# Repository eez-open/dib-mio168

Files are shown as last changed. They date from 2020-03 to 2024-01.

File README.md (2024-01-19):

### Ownership and License
The contributors are listed in CONTRIB.TXT.

Licenses | OSHWA UID
--|--
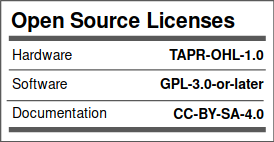
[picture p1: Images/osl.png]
osl
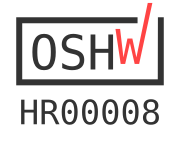
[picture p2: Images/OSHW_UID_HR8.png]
OSHW-HR000008 (https://certification.oshwa.org/hr000008.html)
 | 

### Overview

The [EEZ DIB](https://github.com/eez-open/modular-psu) MIO168 module features multiple digital I/O, analog outputs and expansion connectors for carry various AFEs.

### Feature list

* On-board [STM32F446ZCT6](https://www.st.com/content/st_com/en/products/microcontrollers-microprocessors/stm32-32-bit-arm-cortex-mcus/stm32-high-performance-mcus/stm32f4-series/stm32f446/stm32f446zc.html) high-performance foundation line MCU, ARM Cortex-M4 with DSP and FPU, 256 KiB Flash, LQFP-144 package 
* 1 x 8-pin single row 3.81 mm connector (digital inputs)
* 1 x 16-pin dual row 3.81 mm I/O connector (digital and analog outputs)
* 2 x 10-pin ADIB 2.0 mm connectors
* 8 x protected digital inputs (3.3/5/24 V), 2 x fast/slow, 6 x slow
* 8 x digital outputs (low-side) with multiple protections, voltage clamp 42V, current limit 10 A
* 2 x PWM outputs (protected) or sensor bias power (+/-15 V, max. 10 mA)
* 2 x analog bipolar outputs (+/-5 V, +/-10 V, 0-5 V, 0-10 V). Voltage or current output with protection. 12-bit DAC, replaceable with pin compatible 14- or 16-bit version
* 2 x analog bipolar outputs +/-10 V. 12-bit DAC, replaceable with pin compatible 14- or 16-bit version
* On-board isolated power supply with +/-5.3 V outputs (with 4x multipliers), +/-15 V and +3.3 V LDO
* Firmware download via SPI
* Optional SWD for debugging
* I2C EEPROM for storing board specific parameters
* Dimensions: 146 x 95 mm, 4-layer PCB

### r3B1 prototype 3D model (without AFE installed)

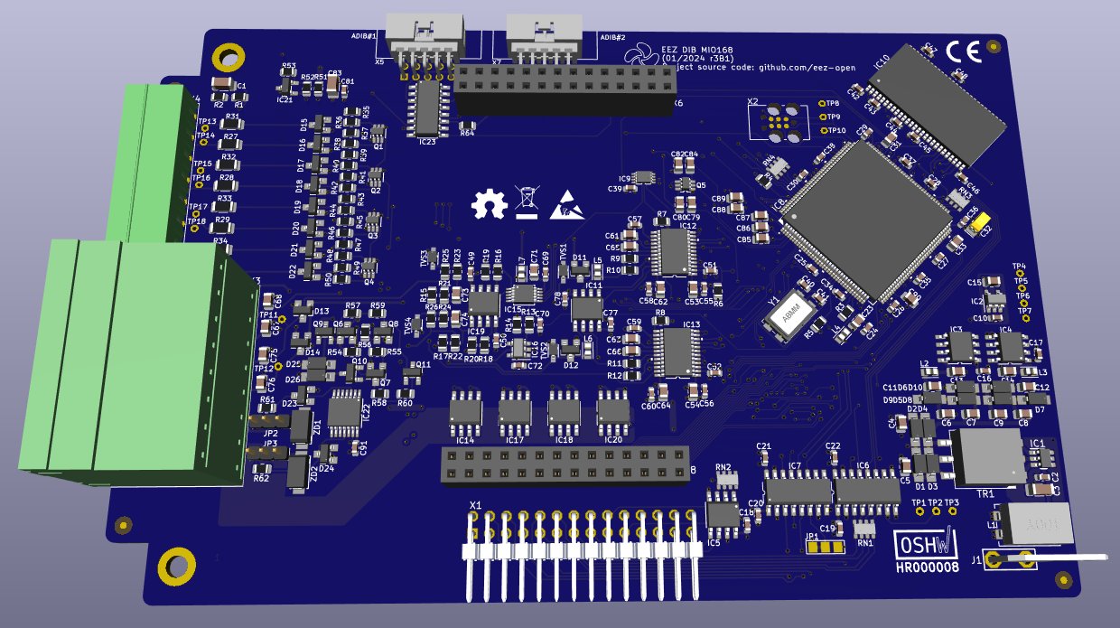
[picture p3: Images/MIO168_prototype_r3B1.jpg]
prototype


### Firmware repository

https://github.com/eez-open/dib-mio168-fw  
The firmware download procedure is described in [Chapter 13.2](https://www.envox.eu/eez-bench-box-3/bb3-user-manual/13-firmware-upgrade/#bb3_man_module_upgrade) of the User Manual.  
The MIO168 module GUI is described in [Chapter 19](https://www.envox.eu/eez-bench-box-3/bb3-user-manual/19-mio168-mixed-input-output-module/) of the User Manual. 

### KiCad project (v7 or newer)

* [MIO168 r3B1](https://github.com/eez-open/dib-mio168/tree/master/EDA%20files/KiCad)

All symbols, footprints and 3D models used in the project can be found in the [EEZ-DIB Library](https://github.com/eez-open/eez-kicad-libraries) plugin for KiCad.

### Bill of materials

* [Download](https://github.com/eez-open/dib-mio168/tree/master/EDA%20files/KiCad/bom/ibom.html) as raw file _Interactive BOM_ (ibom.html) and open it locally in your browser.

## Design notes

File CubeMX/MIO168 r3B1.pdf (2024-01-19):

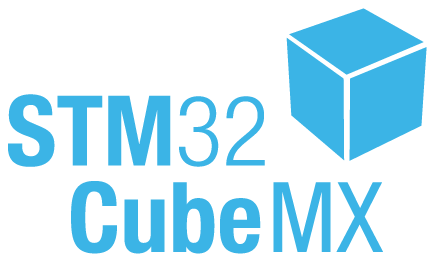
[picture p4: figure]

19/01/2024

MIO168 r3B1 Project
Configuration Report

## 1. Description

### 1.1. Project

Project Name | MIO168 r3B1
Board Name | custom
Generated with: | STM32CubeMX 6.10.0
Date | 01/19/2024

### 1.2. MCU

MCU Series | STM32F4
MCU Line | STM32F446
MCU name | STM32F446ZCTx
MCU Package | LQFP144
MCU Pin number | 144

### 1.3. Core(s) information

Core(s) | Arm Cortex-M4

## 2. Pinout Configuration

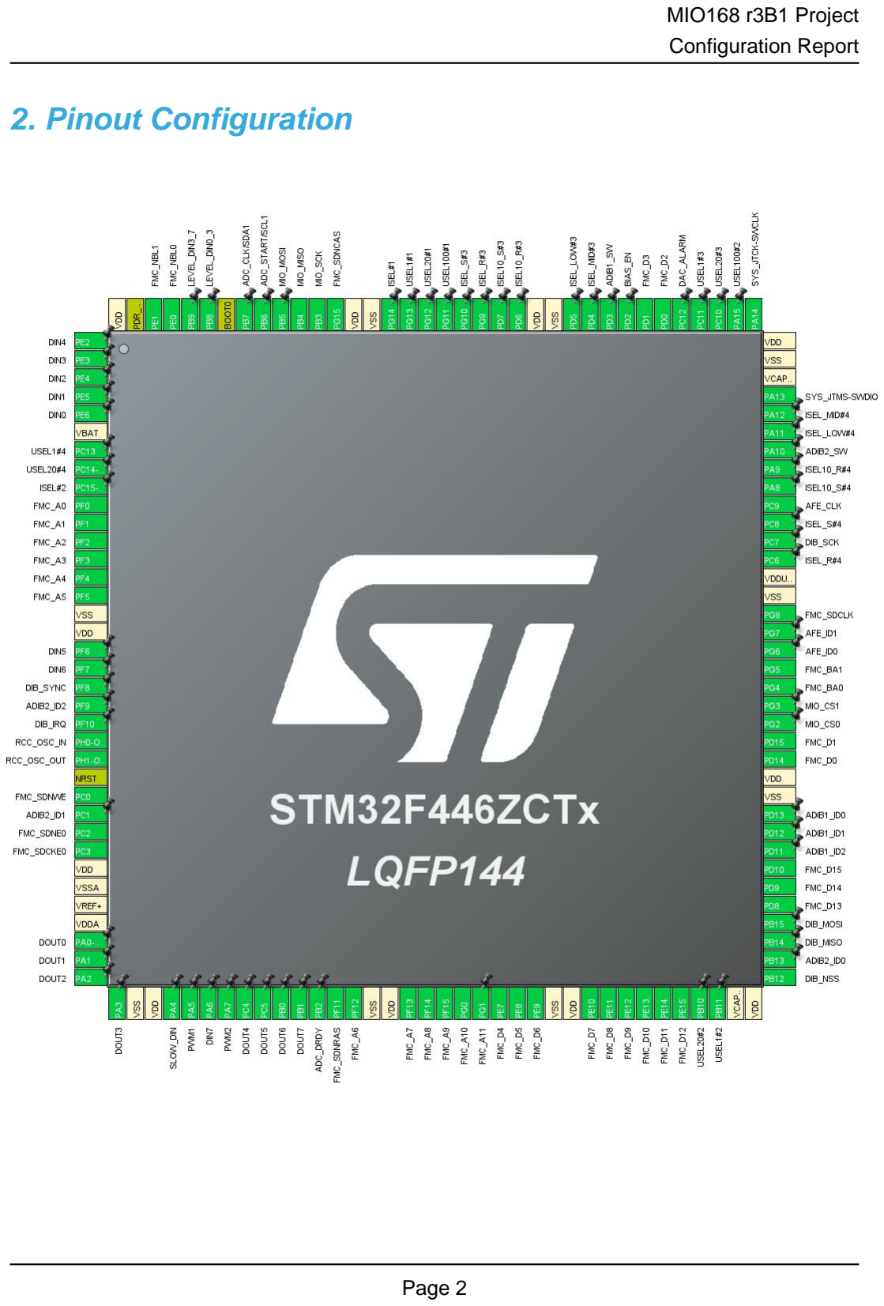
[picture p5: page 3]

## 3. Pins Configuration

Pin Number LQFP144 | Pin Name (function after reset) | Pin Type | Alternate Function(s) | Label
1 | PE2 * | I/O | GPIO_Input | DIN4
2 | PE3 * | I/O | GPIO_Input | DIN3
3 | PE4 * | I/O | GPIO_Input | DIN2
4 | PE5 | I/O | TIM9_CH1 | DIN1
5 | PE6 | I/O | TIM9_CH2 | DIN0
6 | VBAT | Power
7 | PC13 * | I/O | GPIO_Output | USEL1#4
8 | PC14-OSC32_IN * | I/O | GPIO_Output | USEL20#4
9 | PC15-OSC32_OUT * | I/O | GPIO_Output | ISEL#2
10 | PF0 | I/O | FMC_A0
11 | PF1 | I/O | FMC_A1
12 | PF2 | I/O | FMC_A2
13 | PF3 | I/O | FMC_A3
14 | PF4 | I/O | FMC_A4
15 | PF5 | I/O | FMC_A5
16 | VSS | Power
17 | VDD | Power
18 | PF6 * | I/O | GPIO_Input | DIN5
19 | PF7 * | I/O | GPIO_Input | DIN6
20 | PF8 * | I/O | GPIO_Input | DIB_SYNC
21 | PF9 * | I/O | GPIO_Input | ADIB2_ID2
22 | PF10 * | I/O | GPIO_Output | DIB_IRQ
23 | PH0-OSC_IN | I/O | RCC_OSC_IN
24 | PH1-OSC_OUT | I/O | RCC_OSC_OUT
25 | NRST | Reset
26 | PC0 | I/O | FMC_SDNWE
27 | PC1 * | I/O | GPIO_Input | ADIB2_ID1
28 | PC2 | I/O | FMC_SDNE0
29 | PC3 | I/O | FMC_SDCKE0
30 | VDD | Power
31 | VSSA | Power
32 | VREF+ | Power
33 | VDDA | Power
34 | PA0-WKUP * | I/O | GPIO_Output | DOUT0
35 | PA1 * | I/O | GPIO_Output | DOUT1
36 | PA2 * | I/O | GPIO_Output | DOUT2

Pin Number LQFP144 | Pin Name (function after reset) | Pin Type | Alternate Function(s) | Label
37 | PA3 * | I/O | GPIO_Output | DOUT3
38 | VSS | Power
39 | VDD | Power
40 | PA4 * | I/O | GPIO_Output | SLOW_DIN
41 | PA5 | I/O | TIM2_CH1 | PWM1
42 | PA6 * | I/O | GPIO_Input | DIN7
43 | PA7 | I/O | TIM3_CH2 | PWM2
44 | PC4 * | I/O | GPIO_Output | DOUT4
45 | PC5 * | I/O | GPIO_Output | DOUT5
46 | PB0 * | I/O | GPIO_Output | DOUT6
47 | PB1 * | I/O | GPIO_Output | DOUT7
48 | PB2 * | I/O | GPIO_Input | ADC_DRDY
49 | PF11 | I/O | FMC_SDNRAS
50 | PF12 | I/O | FMC_A6
51 | VSS | Power
52 | VDD | Power
53 | PF13 | I/O | FMC_A7
54 | PF14 | I/O | FMC_A8
55 | PF15 | I/O | FMC_A9
56 | PG0 | I/O | FMC_A10
57 | PG1 | I/O | FMC_A11
58 | PE7 | I/O | FMC_D4
59 | PE8 | I/O | FMC_D5
60 | PE9 | I/O | FMC_D6
61 | VSS | Power
62 | VDD | Power
63 | PE10 | I/O | FMC_D7
64 | PE11 | I/O | FMC_D8
65 | PE12 | I/O | FMC_D9
66 | PE13 | I/O | FMC_D10
67 | PE14 | I/O | FMC_D11
68 | PE15 | I/O | FMC_D12
69 | PB10 * | I/O | GPIO_Output | USEL20#2
70 | PB11 * | I/O | GPIO_Output | USEL1#2
71 | VCAP_1 | Power
72 | VDD | Power
73 | PB12 | I/O | SPI2_NSS | DIB_NSS
74 | PB13 * | I/O | GPIO_Input | ADIB2_ID0
75 | PB14 | I/O | SPI2_MISO | DIB_MISO

Pin Number LQFP144 | Pin Name (function after reset) | Pin Type | Alternate Function(s) | Label
76 | PB15 | I/O | SPI2_MOSI | DIB_MOSI
77 | PD8 | I/O | FMC_D13
78 | PD9 | I/O | FMC_D14
79 | PD10 | I/O | FMC_D15
80 | PD11 * | I/O | GPIO_Input | ADIB1_ID2
81 | PD12 * | I/O | GPIO_Input | ADIB1_ID1
82 | PD13 * | I/O | GPIO_Input | ADIB1_ID0
83 | VSS | Power
84 | VDD | Power
85 | PD14 | I/O | FMC_D0
86 | PD15 | I/O | FMC_D1
87 | PG2 * | I/O | GPIO_Output | MIO_CS0
88 | PG3 * | I/O | GPIO_Output | MIO_CS1
89 | PG4 | I/O | FMC_BA0
90 | PG5 | I/O | FMC_BA1
91 | PG6 * | I/O | GPIO_Input | AFE_ID0
92 | PG7 * | I/O | GPIO_Input | AFE_ID1
93 | PG8 | I/O | FMC_SDCLK
94 | VSS | Power
95 | VDDUSB | Power
96 | PC6 * | I/O | GPIO_Output | ISEL_R#4
97 | PC7 | I/O | SPI2_SCK | DIB_SCK
98 | PC8 * | I/O | GPIO_Output | ISEL_S#4
99 | PC9 | I/O | RCC_MCO_2 | AFE_CLK
100 | PA8 * | I/O | GPIO_Output | ISEL10_S#4
101 | PA9 * | I/O | GPIO_Output | ISEL10_R#4
102 | PA10 * | I/O | GPIO_Output | ADIB2_SW
103 | PA11 * | I/O | GPIO_Output | ISEL_LOW#4
104 | PA12 * | I/O | GPIO_Output | ISEL_MID#4
105 | PA13 | I/O | SYS_JTMS-SWDIO
106 | VCAP_2 | Power
107 | VSS | Power
108 | VDD | Power
109 | PA14 | I/O | SYS_JTCK-SWCLK
110 | PA15 * | I/O | GPIO_Output | USEL100#2
111 | PC10 * | I/O | GPIO_Output | USEL20#3
112 | PC11 * | I/O | GPIO_Output | USEL1#3
113 | PC12 * | I/O | GPIO_Input | DAC_ALARM
114 | PD0 | I/O | FMC_D2

Pin Number LQFP144 | Pin Name (function after reset) | Pin Type | Alternate Function(s) | Label
115 | PD1 | I/O | FMC_D3
116 | PD2 * | I/O | GPIO_Output | BIAS_EN
117 | PD3 * | I/O | GPIO_Output | ADIB1_SW
118 | PD4 * | I/O | GPIO_Output | ISEL_MID#3
119 | PD5 * | I/O | GPIO_Output | ISEL_LOW#3
120 | VSS | Power
121 | VDD | Power
122 | PD6 * | I/O | GPIO_Output | ISEL10_R#3
123 | PD7 * | I/O | GPIO_Output | ISEL10_S#3
124 | PG9 * | I/O | GPIO_Output | ISEL_R#3
125 | PG10 * | I/O | GPIO_Output | ISEL_S#3
126 | PG11 * | I/O | GPIO_Output | USEL100#1
127 | PG12 * | I/O | GPIO_Output | USEL20#1
128 | PG13 * | I/O | GPIO_Output | USEL1#1
129 | PG14 * | I/O | GPIO_Output | ISEL#1
130 | VSS | Power
131 | VDD | Power
132 | PG15 | I/O | FMC_SDNCAS
133 | PB3 | I/O | SPI3_SCK | MIO_SCK
134 | PB4 | I/O | SPI3_MISO | MIO_MISO
135 | PB5 | I/O | SPI3_MOSI | MIO_MOSI
136 | PB6 * | I/O | GPIO_Output | ADC_START/SCL1
137 | PB7 * | I/O | GPIO_Output | ADC_CLK/SDA1
138 | BOOT0 | Boot
139 | PB8 * | I/O | GPIO_Output | LEVEL_DIN0_3
140 | PB9 * | I/O | GPIO_Output | LEVEL_DIN3_7
141 | PE0 | I/O | FMC_NBL0
142 | PE1 | I/O | FMC_NBL1
143 | PDR_ON | Reset
144 | VDD | Power

* The pin is affected with an I/O function

## 4. Clock Tree Configuration

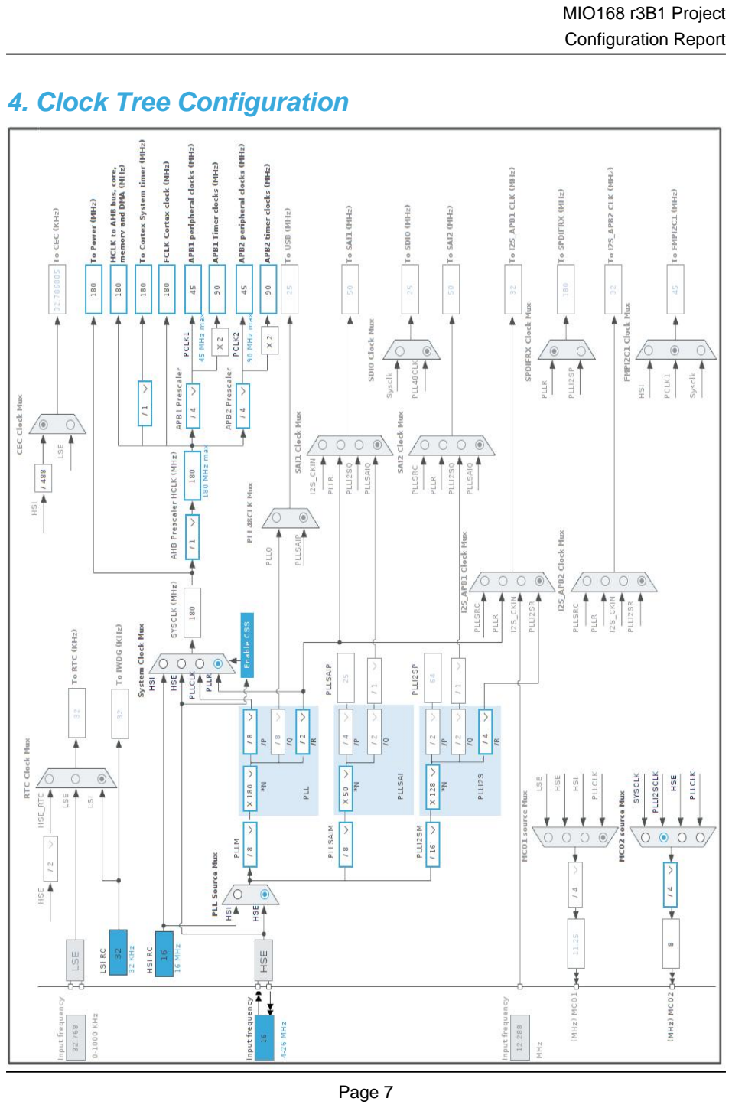
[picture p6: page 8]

## 5. Software Project

### 5.1. Project Settings

Name | Value
Project Name | MIO168 r3B1
Project Folder | /home/denis/git-public/dib-mio168/CubeMX
Toolchain / IDE | STM32CubeIDE
Firmware Package Name and Version | STM32Cube FW_F4 V1.26.1
Application Structure | Advanced
Generate Under Root | Yes
Do not generate the main() | No
Minimum Heap Size | 0x2000
Minimum Stack Size | 0x4000

### 5.2. Code Generation Settings

Name | Value
STM32Cube MCU packages and embedded software | Copy only the necessary library files
Generate peripheral initialization as a pair of '.c/.h' files | No
Backup previously generated files when re-generating | No
Keep User Code when re-generating | Yes
Delete previously generated files when not re-generated | Yes
Set all free pins as analog (to optimize the power consumption) | No
Enable Full Assert | No

### 5.3. Advanced Settings - Generated Function Calls

Rank | Function Name | Peripheral Instance Name
1 | MX_GPIO_Init | GPIO
2 | MX_DMA_Init | DMA
3 | SystemClock_Config | RCC
4 | MX_CRC_Init | CRC
5 | MX_SPI2_Init | SPI2
6 | MX_SPI3_Init | SPI3
7 | MX_TIM9_Init | TIM9
8 | MX_TIM6_Init | TIM6
9 | MX_TIM2_Init | TIM2
10 | MX_TIM3_Init | TIM3
11 | MX_TIM7_Init | TIM7

Rank | Function Name | Peripheral Instance Name
12 | MX_FMC_Init | FMC

## 1. Power Consumption Calculator report

### 1.1. Microcontroller Selection

Series | STM32F4
Line | STM32F446
MCU | STM32F446ZCTx
Datasheet | DS10693_Rev6

### 1.2. Parameter Selection

Temperature | 25
Vdd | 3.3

### 1.3. Battery Selection

Battery | Li-SOCL2(A3400)
Capacity | 3400.0 mAh
Self Discharge | 0.08 %/month
Nominal Voltage | 3.6 V
Max Cont Current | 100.0 mA
Max Pulse Current | 200.0 mA
Cells in series | 1
Cells in parallel | 1

### 1.4. Sequence

Step | Step1 | Step2
Mode | RUN | STOP_UDM (Under Drive)
Vdd | 3.3 | 3.3
Voltage Source | Battery | Battery
Range | Scale1-High | No Scale
Fetch Type | RAM/FLASH/REGON/ART/P REFETCH | n/a
CPU Frequency | 180 MHz | 0 Hz
Clock Configuration | HSE PLL | Regulator_LP Flash-PwrDwn
Clock Source Frequency | 4 MHz | 0 Hz
Peripherals
Additional Cons. | 0 mA | 0 mA
Average Current | 46 mA | 55 µA
Duration | 0.1 ms | 0.9 ms
DMIPS | 225.0 | 0.0
Ta Max | 99.99 | 104.99
Category | In DS Table | In DS Table

### 1.5. Results

Sequence Time | 1 ms | Average Current | 4.65 mA
Battery Life | 1 month | Average DMIPS | 225.0 DMIPS

### 1.6. Chart

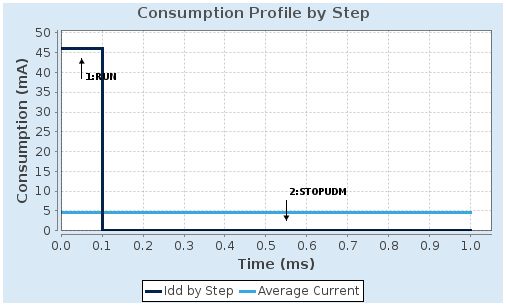
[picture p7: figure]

## 2. Peripherals and Middlewares Configuration

### 2.1. CRC

mode: Activated

### 2.2. FMC

SDRAM 1
Clock and chip enable: SDCKE0+SDNE0 Internal bank number: 4 banks Address: 12 bits
Data: 16 bits
Byte enable: set
2.2.1. SDRAM 1:

SDRAM control:

Bank | SDRAM bank 1
Number of column address bits | 8 bits
Number of row address bits | 12 bits
CAS latency | 1 memory clock cycle
Write protection | Disabled
SDRAM common clock | Disabled
SDRAM common burst read | Disabled
SDRAM common read pipe delay | 0 HCLK clock cycle
SDRAM timing in memory clock cycles:
Load mode register to active delay | 16
Exit self-refresh delay | 16
Self-refresh time | 16
SDRAM common row cycle delay | 16
Write recovery time | 16
SDRAM common row precharge delay | 16
Row to column delay | 16

### 2.3. RCC

High Speed Clock (HSE): Crystal/Ceramic Resonator mode: Master Clock Output 2
2.3.1. Parameter Settings:

System Parameters:

VDD voltage (V) | 3.3
Instruction Cache | Enabled
Prefetch Buffer | Enabled
Data Cache | Enabled
Flash Latency(WS) | 5 WS (6 CPU cycle)
RCC Parameters:
HSI Calibration Value | 16
TIM Prescaler Selection | Disabled
HSE Startup Timout Value (ms) | 100
LSE Startup Timout Value (ms) | 5000
Power Parameters:
Power Regulator Voltage Scale | Power Regulator Voltage Scale 1
Power Over Drive | Enabled

### 2.4. SPI2

Mode: Full-Duplex Slave
Hardware NSS Signal: Hardware NSS Input Signal
2.4.1. Parameter Settings:

Basic Parameters:

Frame Format | Motorola
Data Size | 8 Bits
First Bit | MSB First
Clock Parameters:
Clock Polarity (CPOL) | Low
Clock Phase (CPHA) | 1 Edge
Advanced Parameters:
CRC Calculation | Disabled
NSS Signal Type | Input Hardware

### 2.5. SPI3

Mode: Full-Duplex Master
2.5.1. Parameter Settings:

Basic Parameters:

Frame Format | Motorola
Data Size | 8 Bits

First Bit | MSB First
Clock Parameters:
Prescaler (for Baud Rate) | 2
Baud Rate | 22.5 MBits/s *
Clock Polarity (CPOL) | Low
Clock Phase (CPHA) | 2 Edge *
Advanced Parameters:
CRC Calculation | Disabled
NSS Signal Type | Software

### 2.6. SYS

Debug: Serial Wire
Timebase Source: SysTick

### 2.7. TIM2

Channel1: PWM Generation CH1
2.7.1. Parameter Settings:

Counter Settings:

Prescaler (PSC - 16 bits value) | 0
Counter Mode | Up
Counter Period (AutoReload Register - 32 bits value ) | 0 *
Internal Clock Division (CKD) | No Division
auto-reload preload | Disable
Trigger Output (TRGO) Parameters:
Master/Slave Mode (MSM bit) | Disable (Trigger input effect not delayed)
Trigger Event Selection | Reset (UG bit from TIMx_EGR)
PWM Generation Channel 1:
Mode | PWM mode 1
Pulse (32 bits value) | 0
Output compare preload | Enable
Fast Mode | Disable
CH Polarity | High

### 2.8. TIM3

Channel2: PWM Generation CH2
2.8.1. Parameter Settings:

Counter Settings:

Prescaler (PSC - 16 bits value) | 0
Counter Mode | Up
Counter Period (AutoReload Register - 16 bits value ) | 0 *
Internal Clock Division (CKD) | No Division
auto-reload preload | Disable
Trigger Output (TRGO) Parameters:
Master/Slave Mode (MSM bit) | Disable (Trigger input effect not delayed)
Trigger Event Selection | Reset (UG bit from TIMx_EGR)
PWM Generation Channel 2:
Mode | PWM mode 1
Pulse (16 bits value) | 0
Output compare preload | Enable
Fast Mode | Disable
CH Polarity | High

### 2.9. TIM6

mode: Activated
2.9.1. Parameter Settings:

Counter Settings:

Prescaler (PSC - 16 bits value) | 8 *
Counter Mode | Up
Counter Period (AutoReload Register - 16 bits value ) | 999 *
auto-reload preload | Enable *
Trigger Output (TRGO) Parameters:
Trigger Event Selection | Reset (UG bit from TIMx_EGR)

### 2.10. TIM7

mode: Activated
2.10.1. Parameter Settings:

Counter Settings:

Prescaler (PSC - 16 bits value) | 8 *
Counter Mode | Up
Counter Period (AutoReload Register - 16 bits value ) | 999 *
auto-reload preload | Enable *
Trigger Output (TRGO) Parameters:
Trigger Event Selection | Reset (UG bit from TIMx_EGR)

### 2.11. TIM9

Channel1: Input Capture direct mode
Channel2: Input Capture direct mode
2.11.1. Parameter Settings:

Counter Settings:

Prescaler (PSC - 16 bits value) | 0
Counter Mode | Up
Counter Period (AutoReload Register - 16 bits value ) | 0 *
Internal Clock Division (CKD) | No Division
auto-reload preload | Disable
Input Capture Channel 1:
Polarity Selection | Rising Edge
IC Selection | Direct
Prescaler Division Ratio | No division
Input Filter (4 bits value) | 0
Input Capture Channel 2:
Polarity Selection | Rising Edge
IC Selection | Direct
Prescaler Division Ratio | No division
Input Filter (4 bits value) | 0

* User modified value

## 3. System Configuration

### 3.1. GPIO configuration

IP | Pin | Signal | GPIO mode | GPIO pull/up pull down

Max
Speed

User Label

FMC | PF0 | FMC_A0 | Alternate Function Push Pull | No pull-up and no pull-down | Very High
| PF1 | FMC_A1 | Alternate Function Push Pull | No pull-up and no pull-down | Very High
| PF2 | FMC_A2 | Alternate Function Push Pull | No pull-up and no pull-down | Very High
| PF3 | FMC_A3 | Alternate Function Push Pull | No pull-up and no pull-down | Very High
| PF4 | FMC_A4 | Alternate Function Push Pull | No pull-up and no pull-down | Very High
| PF5 | FMC_A5 | Alternate Function Push Pull | No pull-up and no pull-down | Very High
PC0 | FMC_SDNWE Alternate Function Push Pull | No pull-up and no pull-down | Very High
| PC2 | FMC_SDNE0 | Alternate Function Push Pull | No pull-up and no pull-down | Very High
PC3 | FMC_SDCKE0 Alternate Function Push Pull | No pull-up and no pull-down | Very High
PF11 | FMC_SDNRAS Alternate Function Push Pull | No pull-up and no pull-down | Very High
| PF12 | FMC_A6 | Alternate Function Push Pull | No pull-up and no pull-down | Very High
| PF13 | FMC_A7 | Alternate Function Push Pull | No pull-up and no pull-down | Very High
| PF14 | FMC_A8 | Alternate Function Push Pull | No pull-up and no pull-down | Very High
| PF15 | FMC_A9 | Alternate Function Push Pull | No pull-up and no pull-down | Very High
| PG0 | FMC_A10 | Alternate Function Push Pull | No pull-up and no pull-down | Very High
| PG1 | FMC_A11 | Alternate Function Push Pull | No pull-up and no pull-down | Very High
| PE7 | FMC_D4 | Alternate Function Push Pull | No pull-up and no pull-down | Very High
| PE8 | FMC_D5 | Alternate Function Push Pull | No pull-up and no pull-down | Very High
| PE9 | FMC_D6 | Alternate Function Push Pull | No pull-up and no pull-down | Very High
| PE10 | FMC_D7 | Alternate Function Push Pull | No pull-up and no pull-down | Very High
| PE11 | FMC_D8 | Alternate Function Push Pull | No pull-up and no pull-down | Very High
| PE12 | FMC_D9 | Alternate Function Push Pull | No pull-up and no pull-down | Very High
| PE13 | FMC_D10 | Alternate Function Push Pull | No pull-up and no pull-down | Very High
| PE14 | FMC_D11 | Alternate Function Push Pull | No pull-up and no pull-down | Very High
| PE15 | FMC_D12 | Alternate Function Push Pull | No pull-up and no pull-down | Very High
| PD8 | FMC_D13 | Alternate Function Push Pull | No pull-up and no pull-down | Very High
| PD9 | FMC_D14 | Alternate Function Push Pull | No pull-up and no pull-down | Very High
| PD10 | FMC_D15 | Alternate Function Push Pull | No pull-up and no pull-down | Very High
| PD14 | FMC_D0 | Alternate Function Push Pull | No pull-up and no pull-down | Very High
| PD15 | FMC_D1 | Alternate Function Push Pull | No pull-up and no pull-down | Very High
| PG4 | FMC_BA0 | Alternate Function Push Pull | No pull-up and no pull-down | Very High
| PG5 | FMC_BA1 | Alternate Function Push Pull | No pull-up and no pull-down | Very High
| PG8 | FMC_SDCLK | Alternate Function Push Pull | No pull-up and no pull-down | Very High
| PD0 | FMC_D2 | Alternate Function Push Pull | No pull-up and no pull-down | Very High
| PD1 | FMC_D3 | Alternate Function Push Pull | No pull-up and no pull-down | Very High
PG15 | FMC_SDNCAS Alternate Function Push Pull | No pull-up and no pull-down | Very High

IP | Pin | Signal | GPIO mode | GPIO pull/up pull down

Max
Speed

User Label

| PE0 | FMC_NBL0 | Alternate Function Push Pull | No pull-up and no pull-down | Very High
| PE1 | FMC_NBL1 | Alternate Function Push Pull | No pull-up and no pull-down | Very High
RCC | PH0- OSC_IN | RCC_OSC_IN | n/a | n/a | n/a
| PH1- OSC_OUT | RCC_OSC_OUT | n/a | n/a | n/a
| PC9 | RCC_MCO_2 | Alternate Function Push Pull | No pull-up and no pull-down | Low | AFE_CLK
SPI2 | PB12 | SPI2_NSS | Alternate Function Push Pull | No pull-up and no pull-down | Very High
*
| | | | | | DIB_NSS
| PB14 | SPI2_MISO | Alternate Function Push Pull | No pull-up and no pull-down | Very High
*
| | | | | | DIB_MISO
| PB15 | SPI2_MOSI | Alternate Function Push Pull | No pull-up and no pull-down | Very High
*
| | | | | | DIB_MOSI
| PC7 | SPI2_SCK | Alternate Function Push Pull | No pull-up and no pull-down | Very High
*
| | | | | | DIB_SCK
SPI3 | PB3 | SPI3_SCK | Alternate Function Push Pull | No pull-up and no pull-down | Very High
*
| | | | | | MIO_SCK
| PB4 | SPI3_MISO | Alternate Function Push Pull | No pull-up and no pull-down | Very High
*
| | | | | | MIO_MISO
| PB5 | SPI3_MOSI | Alternate Function Push Pull | No pull-up and no pull-down | Very High
*
| | | | | | MIO_MOSI
SYS | PA13 | SYS_JTMS- SWDIO | n/a | n/a | n/a
| PA14 | SYS_JTCK- SWCLK | n/a | n/a | n/a
TIM2 | PA5 | TIM2_CH1 | Alternate Function Push Pull | No pull-up and no pull-down | Low | PWM1
TIM3 | PA7 | TIM3_CH2 | Alternate Function Push Pull | No pull-up and no pull-down | Low | PWM2
TIM9 | PE5 | TIM9_CH1 | Alternate Function Push Pull | No pull-up and no pull-down | Low | DIN1
| PE6 | TIM9_CH2 | Alternate Function Push Pull | No pull-up and no pull-down | Low | DIN0
GPIO | PE2 | GPIO_Input | Input mode | No pull-up and no pull-down | n/a | DIN4
| PE3 | GPIO_Input | Input mode | No pull-up and no pull-down | n/a | DIN3
| PE4 | GPIO_Input | Input mode | No pull-up and no pull-down | n/a | DIN2
| PC13 | GPIO_Output | Output Push Pull | No pull-up and no pull-down | Low | USEL1#4
| PC14- OSC32_IN | GPIO_Output | Output Push Pull | No pull-up and no pull-down | Low | USEL20#4
| PC15- OSC32_OU T | GPIO_Output | Output Push Pull | No pull-up and no pull-down | Low | ISEL#2
PF6 | GPIO_Input | Input mode | No pull-up and no pull-down | n/a | DIN5
PF7 | GPIO_Input | Input mode | No pull-up and no pull-down | n/a | DIN6

IP | Pin | Signal | GPIO mode | GPIO pull/up pull down | Max Speed | User Label
| PF8 | GPIO_Input | Input mode | No pull-up and no pull-down | n/a | DIB_SYNC
| PF9 | GPIO_Input | Input mode | No pull-up and no pull-down | n/a | ADIB2_ID2
| PF10 | GPIO_Output | Output Push Pull | No pull-up and no pull-down | Low | DIB_IRQ
| PC1 | GPIO_Input | Input mode | No pull-up and no pull-down | n/a | ADIB2_ID1
| PA0-WKUP | GPIO_Output | Output Push Pull | No pull-up and no pull-down | Low | DOUT0
| PA1 | GPIO_Output | Output Push Pull | No pull-up and no pull-down | Low | DOUT1
| PA2 | GPIO_Output | Output Push Pull | No pull-up and no pull-down | Low | DOUT2
| PA3 | GPIO_Output | Output Push Pull | No pull-up and no pull-down | Low | DOUT3
| PA4 | GPIO_Output | Output Push Pull | No pull-up and no pull-down | Low | SLOW_DIN
| PA6 | GPIO_Input | Input mode | No pull-up and no pull-down | n/a | DIN7
| PC4 | GPIO_Output | Output Push Pull | No pull-up and no pull-down | Low | DOUT4
| PC5 | GPIO_Output | Output Push Pull | No pull-up and no pull-down | Low | DOUT5
| PB0 | GPIO_Output | Output Push Pull | No pull-up and no pull-down | Low | DOUT6
| PB1 | GPIO_Output | Output Push Pull | No pull-up and no pull-down | Low | DOUT7
| PB2 | GPIO_Input | Input mode | No pull-up and no pull-down | n/a | ADC_DRDY
| PB10 | GPIO_Output | Output Push Pull | No pull-up and no pull-down | Low | USEL20#2
| PB11 | GPIO_Output | Output Push Pull | No pull-up and no pull-down | Low | USEL1#2
| PB13 | GPIO_Input | Input mode | No pull-up and no pull-down | n/a | ADIB2_ID0
| PD11 | GPIO_Input | Input mode | Pull-up * | n/a | ADIB1_ID2
| PD12 | GPIO_Input | Input mode | Pull-up * | n/a | ADIB1_ID1
| PD13 | GPIO_Input | Input mode | Pull-up * | n/a | ADIB1_ID0
| PG2 | GPIO_Output | Output Push Pull | No pull-up and no pull-down | Low | MIO_CS0
| PG3 | GPIO_Output | Output Push Pull | No pull-up and no pull-down | Low | MIO_CS1
| PG6 | GPIO_Input | Input mode | No pull-up and no pull-down | n/a | AFE_ID0
| PG7 | GPIO_Input | Input mode | No pull-up and no pull-down | n/a | AFE_ID1
| PC6 | GPIO_Output | Output Push Pull | No pull-up and no pull-down | Low | ISEL_R#4
| PC8 | GPIO_Output | Output Push Pull | No pull-up and no pull-down | Low | ISEL_S#4
| PA8 | GPIO_Output | Output Push Pull | No pull-up and no pull-down | Low | ISEL10_S#4
| PA9 | GPIO_Output | Output Push Pull | No pull-up and no pull-down | Low | ISEL10_R#4
| PA10 | GPIO_Output | Output Push Pull | No pull-up and no pull-down | Low | ADIB2_SW
| PA11 | GPIO_Output | Output Push Pull | No pull-up and no pull-down | Low | ISEL_LOW#4
| PA12 | GPIO_Output | Output Push Pull | No pull-up and no pull-down | Low | ISEL_MID#4
| PA15 | GPIO_Output | Output Push Pull | No pull-up and no pull-down | Low | USEL100#2
| PC10 | GPIO_Output | Output Push Pull | No pull-up and no pull-down | Low | USEL20#3
| PC11 | GPIO_Output | Output Push Pull | No pull-up and no pull-down | Low | USEL1#3
| PC12 | GPIO_Input | Input mode | No pull-up and no pull-down | n/a | DAC_ALARM
| PD2 | GPIO_Output | Output Push Pull | No pull-up and no pull-down | Low | BIAS_EN
| PD3 | GPIO_Output | Output Push Pull | No pull-up and no pull-down | Low | ADIB1_SW
| PD4 | GPIO_Output | Output Push Pull | No pull-up and no pull-down | Low | ISEL_MID#3
| PD5 | GPIO_Output | Output Push Pull | No pull-up and no pull-down | Low | ISEL_LOW#3

IP | Pin | Signal | GPIO mode | GPIO pull/up pull down | Max Speed | User Label
| PD6 | GPIO_Output | Output Push Pull | No pull-up and no pull-down | Low | ISEL10_R#3
| PD7 | GPIO_Output | Output Push Pull | No pull-up and no pull-down | Low | ISEL10_S#3
| PG9 | GPIO_Output | Output Push Pull | No pull-up and no pull-down | Low | ISEL_R#3
| PG10 | GPIO_Output | Output Push Pull | No pull-up and no pull-down | Low | ISEL_S#3
| PG11 | GPIO_Output | Output Push Pull | No pull-up and no pull-down | Low | USEL100#1
| PG12 | GPIO_Output | Output Push Pull | No pull-up and no pull-down | Low | USEL20#1
| PG13 | GPIO_Output | Output Push Pull | No pull-up and no pull-down | Low | USEL1#1
| PG14 | GPIO_Output | Output Push Pull | No pull-up and no pull-down | Low | ISEL#1
| PB6 | GPIO_Output | Output Push Pull | No pull-up and no pull-down | Low | ADC_START/SCL1
| PB7 | GPIO_Output | Output Push Pull | No pull-up and no pull-down | Low | ADC_CLK/SDA1
| PB8 | GPIO_Output | Output Push Pull | No pull-up and no pull-down | Low | LEVEL_DIN0_3
| PB9 | GPIO_Output | Output Push Pull | No pull-up and no pull-down | Low | LEVEL_DIN3_7

### 3.2. DMA configuration

DMA request | Stream | Direction | Priority
SPI3_RX | DMA1_Stream0 | Peripheral To Memory | Low
SPI3_TX | DMA1_Stream5 | Memory To Peripheral | Low

SPI3_RX: DMA1_Stream0 DMA request Settings:

Mode: | Normal
Use fifo: | Disable
Peripheral Increment: | Disable
Memory Increment: | Enable *
Peripheral Data Width: | Byte
Memory Data Width: | Byte

SPI3_TX: DMA1_Stream5 DMA request Settings:

Mode: | Normal
Use fifo: | Disable
Peripheral Increment: | Disable
Memory Increment: | Enable *
Peripheral Data Width: | Byte
Memory Data Width: | Byte

### 3.3. NVIC configuration

3.3.1. NVIC
Interrupt Table | Enable | Preenmption Priority | SubPriority
Non maskable interrupt | true | 0 | 0
Hard fault interrupt | true | 0 | 0
Memory management fault | true | 0 | 0
Pre-fetch fault, memory access fault | true | 0 | 0
Undefined instruction or illegal state | true | 0 | 0
System service call via SWI instruction | true | 0 | 0
Debug monitor | true | 0 | 0
Pendable request for system service | true | 0 | 0
System tick timer | true | 0 | 0
DMA1 stream0 global interrupt | true | 0 | 0
DMA1 stream5 global interrupt | true | 0 | 0
TIM6 global interrupt and DAC1, DAC2 underrun error interrupts | true | 0 | 0
TIM7 global interrupt | true | 0 | 0
PVD interrupt through EXTI line 16 | | unused
Flash global interrupt | | unused
RCC global interrupt | | unused
TIM1 break interrupt and TIM9 global interrupt | | unused
TIM2 global interrupt | | unused
TIM3 global interrupt | | unused
SPI2 global interrupt | | unused
FMC global interrupt | | unused
SPI3 global interrupt | | unused
FPU global interrupt | | unused
3.3.2. NVIC Code generation

Enabled interrupt Table Select for init
sequence ordering
| | Generate IRQ
| | handler | Call HAL handler
Non maskable interrupt | false | true | false
Hard fault interrupt | false | true | false
Memory management fault | false | true | false
Pre-fetch fault, memory access fault | false | true | false
Undefined instruction or illegal state | false | true | false
System service call via SWI instruction | false | true | false
Debug monitor | false | true | false
Pendable request for system service | false | true | false
System tick timer | false | true | true

Enabled interrupt Table | Select for init sequence ordering | Generate IRQ handler | Call HAL handler
DMA1 stream0 global interrupt | false | true | true
DMA1 stream5 global interrupt | false | true | true
TIM6 global interrupt and DAC1, DAC2 underrun error interrupts | false | true | true
TIM7 global interrupt | false | true | true

* User modified value

## 4. System Views

4.1. Category view
4.1.1. Current

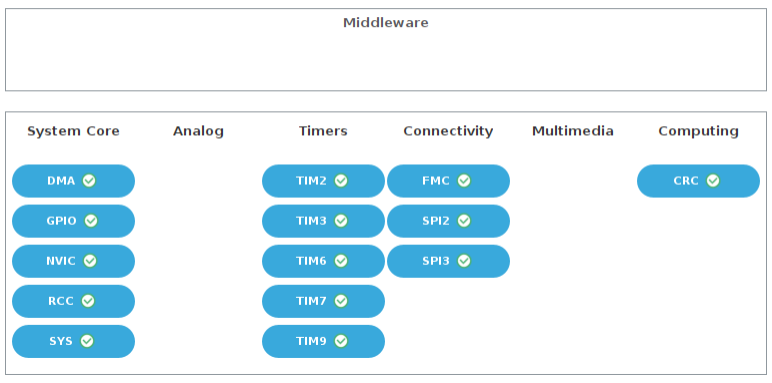
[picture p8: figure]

## 5. Docs & Resources

Type | Link
BSDL files | https://www.st.com/resource/en/bsdl_model/stm32f446_bsdl.zip
IBIS models | https://www.st.com/resource/en/ibis_model/stm32f446_ibis.zip
System View Description | https://www.st.com/resource/en/svd/stm32f4_svd.zip
Presentations | https://www.st.com/resource/en/product_presentation/stm32-stm8_embedded_software_solutions.pdf
Presentations | https://www.st.com/resource/en/product_presentation/stm32_eval-tools_portfolio.pdf
Presentations | https://www.st.com/resource/en/product_presentation/stm32_stm8_functi onal-safety-packages.pdf
Presentations | https://www.st.com/resource/en/product_presentation/stm32-stm8_software_development_tools.pdf
Presentations | https://www.st.com/resource/en/product_presentation/microcontrollers-stm32-family-overview.pdf
Brochures | https://www.st.com/resource/en/brochure/products-and-solutions-for-plcs-and-smart-i-os.pdf
Flyers | https://www.st.com/resource/en/flyer/flstm32nucleo.pdf
Flyers | https://www.st.com/resource/en/flyer/flstmcsuite.pdf
Flyers | https://www.st.com/resource/en/flyer/flstm32trust.pdf
Product Certifications | https://www.st.com/resource/en/certification_document/stm32_authentication_can.pdf
Application Notes | https://www.st.com/resource/en/application_note/an1181-electrostatic-discharge-sensitivity-measurement-stmicroelectronics.pdf
Application Notes | https://www.st.com/resource/en/application_note/an1709-emc-design-guide-for-stm8-stm32-and-legacy-mcus-stmicroelectronics.pdf
Application Notes | https://www.st.com/resource/en/application_note/an2606-stm32-microcontroller-system-memory-boot-mode-stmicroelectronics.pdf
Application Notes | https://www.st.com/resource/en/application_note/an2639-soldering- recommendations-and-package-information-for-leadfree-ecopack-mcus-

| and-mpus-stmicroelectronics.pdf
Application Notes | https://www.st.com/resource/en/application_note/an2867-oscillator-design-guide-for-stm8afals-stm32-mcus-and-mpus-stmicroelectronics.pdf
Application Notes | https://www.st.com/resource/en/application_note/an2945-stm8s-and-stm32-mcus-a-consistent-832bit-product-line-for-painless-migration-stmicroelectronics.pdf
Application Notes | https://www.st.com/resource/en/application_note/an3070-managing-the-driver-enable-signal-for-rs485-and-iolink-communications-with-the-stm32s-usart-stmicroelectronics.pdf
Application Notes | https://www.st.com/resource/en/application_note/an3126-audio-and-waveform-generation-using-the-dac-in-stm32-products-stmicroelectronics.pdf
Application Notes | https://www.st.com/resource/en/application_note/an3154-can-protocol-used-in-the-stm32-bootloader-stmicroelectronics.pdf
Application Notes | https://www.st.com/resource/en/application_note/an3155-usart-protocol-used-in-the-stm32-bootloader-stmicroelectronics.pdf
Application Notes | https://www.st.com/resource/en/application_note/an3156-usb-dfu-protocol-used-in-the-stm32-bootloader-stmicroelectronics.pdf
Application Notes | https://www.st.com/resource/en/application_note/an3364-migration-and-compatibility-guidelines-for-stm32-microcontroller-applications-stmicroelectronics.pdf
Application Notes | https://www.st.com/resource/en/application_note/an3997-audio-playback-and-recording-using-the-stm32f4discovery-stmicroelectronics.pdf
Application Notes | https://www.st.com/resource/en/application_note/an3998-pdm-audio-software-decoding-on-stm32-microcontrollers-stmicroelectronics.pdf
Application Notes | https://www.st.com/resource/en/application_note/an4013-stm32-crossseries-timer-overview-stmicroelectronics.pdf
Application Notes | https://www.st.com/resource/en/application_note/an4031-using-the-stm32f2-stm32f4-and-stm32f7-series-dma-controller-stmicroelectronics.pdf
Application Notes | https://www.st.com/resource/en/application_note/an4221-i2c-protocol-used-in-the-stm32-bootloader-stmicroelectronics.pdf
Application Notes | https://www.st.com/resource/en/application_note/an4229-how-to-

| implement-a-vocoder-solution-using-stm32-microcontrollers-stmicroelectronics.pdf
Application Notes | https://www.st.com/resource/en/application_note/an4277-using-stm32-device-pwm-shutdown-features-for-motor-control-and-digital-power-conversion-stmicroelectronics.pdf
Application Notes | https://www.st.com/resource/en/application_note/an4286-spi-protocol-used-in-the-stm32-bootloader-stmicroelectronics.pdf
Application Notes | https://www.st.com/resource/en/application_note/an4488-getting-started-with-stm32f4xxxx-mcu-hardware-development-stmicroelectronics.pdf
Application Notes | https://www.st.com/resource/en/application_note/an4566-extending-the-dac-performance-of-stm32-microcontrollers-stmicroelectronics.pdf
Application Notes | https://www.st.com/resource/en/application_note/an4640-peripherals-interconnections-on-stm32f4057xx-stm32f4157xx-stm32f42xxx-stm32f43xxx-stm32f446xx-and-stm32f469479xx-stmicroelectronics.pdf
Application Notes | https://www.st.com/resource/en/application_note/an4655-virtually-increasing-the-number-of-serial-communication-peripherals-in-stm32-applications-stmicroelectronics.pdf
Application Notes | https://www.st.com/resource/en/application_note/an4658-migration-of-applications-from-stm32f429439-lines-to-stm32f446-line-stmicroelectronics.pdf
Application Notes | https://www.st.com/resource/en/application_note/an4739-stm32cube-firmware-examples-for-stm32f4-series-stmicroelectronics.pdf
Application Notes | https://www.st.com/resource/en/application_note/an4750-handling-of-soft-errors-in-stm32-applications-stmicroelectronics.pdf
Application Notes | https://www.st.com/resource/en/application_note/an4759-using-the-hardware-realtime-clock-rtc-and-the-tamper-management-unit-tamp-with-stm32-microcontrollers-stmicroelectronics.pdf
Application Notes | https://www.st.com/resource/en/application_note/an4776-generalpurpose-timer-cookbook-for-stm32-microcontrollers-stmicroelectronics.pdf
Application Notes | https://www.st.com/resource/en/application_note/an4803-highspeed-si-simulations-using-ibis-and-boardlevel-simulations-using-hyperlynx-si-on-stm32-mcus-and-mpus-stmicroelectronics.pdf
Application Notes | https://www.st.com/resource/en/application_note/an4850-stm32-mcus-

| spreadspectrum-clock-generation-principles-properties-and-implementation-stmicroelectronics.pdf
Application Notes | https://www.st.com/resource/en/application_note/an4908-stm32-usart-automatic-baud-rate-detection-stmicroelectronics.pdf
Application Notes | https://www.st.com/resource/en/application_note/an4989-stm32-microcontroller-debug-toolbox-stmicroelectronics.pdf
Application Notes | https://www.st.com/resource/en/application_note/an4995-using-an-electromyogram-technique-to-detect-muscle-activity-stmicroelectronics.pdf
Application Notes | https://www.st.com/resource/en/application_note/an5020-digital-camera-interface-dcmi-on-stm32-mcus-stmicroelectronics.pdf
Application Notes | https://www.st.com/resource/en/application_note/an5027-interfacing-pdm-digital-microphones-using-stm32-mcus-and-mpus-stmicroelectronics.pdf
Application Notes | https://www.st.com/resource/en/application_note/an5036-thermal-management-guidelines-for-stm32-applications-stmicroelectronics.pdf
Application Notes | https://www.st.com/resource/en/application_note/an5073-receiving-spdif-audio-stream-with-the-stm32f4f7h7-series-stmicroelectronics.pdf
Application Notes | https://www.st.com/resource/en/application_note/an5543-enhanced-methods-to-handle-spi-communication-on-stm32-devices-stmicroelectronics.pdf
Application Notes | https://www.st.com/resource/en/application_note/an4760-quadspi-interface-on-stm32-microcontrollers-and-microprocessors--stmicroelectronics.pdf
Application Notes | https://www.st.com/resource/en/application_note/an4899-stm32-microcontroller-gpio-hardware-settings-and-lowpower-consumption-stmicroelectronics.pdf
Application Notes | https://www.st.com/resource/en/application_note/an5612-esd-protection-of-stm32-mcus-and-mpus-stmicroelectronics.pdf
Application Notes | https://www.st.com/resource/en/application_note/an5156-introduction-to-stm32-microcontrollers-security-stmicroelectronics.pdf
Application Notes | https://www.st.com/resource/en/application_note/an4838-introduction-to-memory-protection-unit-management-on-stm32-mcus-stmicroelectronics.pdf

Application Notes | https://www.st.com/resource/en/application_note/an4230-random-number-generation-validation-using-nist-statistical-test-suite-for-stm32-microcontrollers-stmicroelectronics.pdf
Application Notes | https://www.st.com/resource/en/application_note/an4879-introduction-to-usb-hardware-and-pcb-guidelines-using-stm32-mcus-stmicroelectronics.pdf
Application Notes | https://www.st.com/resource/en/application_note/an5225-introduction-to-usb-typec-power-delivery-for-stm32-mcus-and-mpus-stmicroelectronics.pdf
Application Notes | https://www.st.com/resource/en/application_note/an2834-how-to-optimize-the-adc-accuracy-in-the-stm32-mcus-stmicroelectronics.pdf
Application Notes | https://www.st.com/resource/en/application_note/an5816-how-to-build-stm32-lpbam-application-using-stm32cubemx-stmicroelectronics.pdf
Application Notes | https://www.st.com/resource/en/application_note/an5537-how-to-use-adc-oversampling-techniques-to-improve-signaltonoise-ratio-on-stm32-mcus-stmicroelectronics.pdf
Application Notes for related Tools & Software | https://www.st.com/resource/en/application_note/an1202_freertos_guide-freertos-guide-stmicroelectronics.pdf
Application Notes for related Tools & Software | https://www.st.com/resource/en/application_note/an1602_semihosting_in_truestudio-how-to-do-semihosting-in-truestudio-stmicroelectronics.pdf
Application Notes for related Tools & Software | https://www.st.com/resource/en/application_note/an1801_stm32cubeprogrammer_in_truestudio-installing-stm32cubeprogrammer-in-truestudio-stmicroelectronics.pdf
Application Notes for related Tools & Software | https://www.st.com/resource/en/application_note/atollic_editing_keyboard_shortcuts-atollic-editing-keyboard-shortcuts-stmicroelectronics.pdf
Application Notes for related Tools & Software | https://www.st.com/resource/en/application_note/iar_to_atollic_truestudio_migration_guide-truestudio-for-arm-migration-guide-iar-embedded-workbench-to-truestudio-stmicroelectronics.pdf
Application Notes for related Tools & Software | https://www.st.com/resource/en/application_note/stm32cubemx_installation_in_truestudio-stm32cubemx-installation-in-truestudio-stmicroelectronics.pdf

Application Notes for related Tools & Software | https://www.st.com/resource/en/application_note/an2656-stm32f10xxx-lcd-glass-driver-firmware-stmicroelectronics.pdf
Application Notes for related Tools & Software | https://www.st.com/resource/en/application_note/an2790-tft-lcd-interfacing-with-the-highdensity-stm32f10xxx-fsmc-stmicroelectronics.pdf
Application Notes for related Tools & Software | https://www.st.com/resource/en/application_note/an3078-stm32-inapplication-programming-over-the-ic-bus-stmicroelectronics.pdf
Application Notes for related Tools & Software | https://www.st.com/resource/en/application_note/an3116-stm32s-adc-modes-and-their-applications-stmicroelectronics.pdf
Application Notes for related Tools & Software | https://www.st.com/resource/en/application_note/an3174-implementing-receivers-for-infrared-remote-control-protocols-using-stm32f10xxx-microcontrollers-stmicroelectronics.pdf
Application Notes for related Tools & Software | https://www.st.com/resource/en/application_note/an3241-qvga-tftlcd-direct-drive-using-the-stm32f10xx-fsmc-peripheral-stmicroelectronics.pdf
Application Notes for related Tools & Software | https://www.st.com/resource/en/application_note/an3307-guidelines-for-obtaining-iec-60335-class-b-certification-for-any-stm32-application-stmicroelectronics.pdf
Application Notes for related Tools & Software | https://www.st.com/resource/en/application_note/an3364-migration-and-compatibility-guidelines-for-stm32-microcontroller-applications-stmicroelectronics.pdf
Application Notes for related Tools & Software | https://www.st.com/resource/en/application_note/an3965-stm32f40xstm32f41x-inapplication-programming-using-the-usart-stmicroelectronics.pdf
Application Notes for related Tools & Software | https://www.st.com/resource/en/application_note/an3969-eeprom-emulation-in-stm32f40xstm32f41x-microcontrollers-stmicroelectronics.pdf
Application Notes for related Tools & Software | https://www.st.com/resource/en/application_note/an3990-upgrading-stm32f4discovery-board-firmware-using-a-usb-key-stmicroelectronics.pdf
Application Notes | https://www.st.com/resource/en/application_note/an3997-audio-playback-

for related Tools & Software | and-recording-using-the-stm32f4discovery-stmicroelectronics.pdf
Application Notes for related Tools & Software | https://www.st.com/resource/en/application_note/an3998-pdm-audio-software-decoding-on-stm32-microcontrollers-stmicroelectronics.pdf
Application Notes for related Tools & Software | https://www.st.com/resource/en/application_note/an4044-floating-point-unit-demonstration-on-stm32-microcontrollers-stmicroelectronics.pdf
Application Notes for related Tools & Software | https://www.st.com/resource/en/application_note/an4323-getting-started-with-stemwin-library-stmicroelectronics.pdf
Application Notes for related Tools & Software | https://www.st.com/resource/en/application_note/an4365-using-stm32f4-mcu-power-modes-with-best-dynamic-efficiency-stmicroelectronics.pdf
Application Notes for related Tools & Software | https://www.st.com/resource/en/application_note/an4435-guidelines-for-obtaining-ulcsaiec-607301603351-class-b-certification-in-any-stm32-application-stmicroelectronics.pdf
Application Notes for related Tools & Software | https://www.st.com/resource/en/application_note/an4457-implementing-an-emulated-uart-on-stm32f4-microcontrollers-stmicroelectronics.pdf
Application Notes for related Tools & Software | https://www.st.com/resource/en/application_note/an4499-stm32--nrf51822-bluetooth-low-energy-system-solution-stmicroelectronics.pdf
Application Notes for related Tools & Software | https://www.st.com/resource/en/application_note/an4657-stm32-inapplication-programming-iap-using-the-usart-stmicroelectronics.pdf
Application Notes for related Tools & Software | https://www.st.com/resource/en/application_note/an4666-parallel-synchronous-transmission-using-gpio-and-dma-stmicroelectronics.pdf
Application Notes for related Tools & Software | https://www.st.com/resource/en/application_note/an4678-full-duplex-spi-emulation-for-stm32f4-microcontrollers-stmicroelectronics.pdf

Application Notes
for related Tools

https://www.st.com/resource/en/application_note/an4701-proprietarycode-readout-protection-on-microcontrollers-of-the-stm32f4-series-

& Software | stmicroelectronics.pdf
Application Notes for related Tools & Software | https://www.st.com/resource/en/application_note/an4739-stm32cube-firmware-examples-for-stm32f4-series-stmicroelectronics.pdf
Application Notes for related Tools & Software | https://www.st.com/resource/en/application_note/an4758-proprietary-code-readout-protection-on-stm32l4-stm32l4-stm32g4-and-stm32wb-series-mcus-stmicroelectronics.pdf
Application Notes for related Tools & Software | https://www.st.com/resource/en/application_note/an4759-using-the-hardware-realtime-clock-rtc-and-the-tamper-management-unit-tamp-with-stm32-microcontrollers-stmicroelectronics.pdf
Application Notes for related Tools & Software | https://www.st.com/resource/en/application_note/an4841-digital-signal-processing-for-stm32-microcontrollers-using-cmsis-stmicroelectronics.pdf
Application Notes for related Tools & Software | https://www.st.com/resource/en/application_note/an4852-programming-an-external-flash-memory-using-the-uart-bootloader-builtin-stm32-microcontrollers-stmicroelectronics.pdf
Application Notes for related Tools & Software | https://www.st.com/resource/en/application_note/an4968-proprietary-code-read-out-protection-pcrop-on-stm32f72xxx-and-stm32f73xxx-microcontrollers-stmicroelectronics.pdf
Application Notes for related Tools & Software | https://www.st.com/resource/en/application_note/an5054-secure-programming-using-stm32cubeprogrammer-stmicroelectronics.pdf
Application Notes for related Tools & Software | https://www.st.com/resource/en/application_note/an5056-integration-guide-for-the-xcubesbsfu-stm32cube-expansion-package-stmicroelectronics.pdf
Application Notes for related Tools & Software | https://www.st.com/resource/en/application_note/an5360-getting-started-with-projects-based-on-the-stm32mp1-series-in-stm32cubeide-stmicroelectronics.pdf
Application Notes for related Tools & Software | https://www.st.com/resource/en/application_note/an5361-getting-started-with-projects-based-on-dualcore-stm32h7-microcontrollers-in-stm32cubeide-stmicroelectronics.pdf
Application Notes for related Tools & Software | https://www.st.com/resource/en/application_note/an5394-getting-started-with-projects-based-on-the-stm32l5-series-in-stm32cubeide-stmicroelectronics.pdf

Application Notes for related Tools & Software | https://www.st.com/resource/en/application_note/an5418-how-to-build-a-simple-usbpd-sink-application-with-stm32cubemx-stmicroelectronics.pdf
Application Notes for related Tools & Software | https://www.st.com/resource/en/application_note/an5426-migrating-graphics-middleware-projects-from-stm32cubemx-540-to-stm32cubemx-550-stmicroelectronics.pdf
Application Notes for related Tools & Software | https://www.st.com/resource/en/application_note/an5464-position-control-of-a-threephase-permanent-magnet-motor-using-xcubemcsdk-or-xcubemcsdkful-stmicroelectronics.pdf
Application Notes for related Tools & Software | https://www.st.com/resource/en/application_note/an5564-getting-started-with-projects-based-on-dualcore-stm32wl-microcontrollers-in-stm32cubeide-stmicroelectronics.pdf
Application Notes for related Tools & Software | https://www.st.com/resource/en/application_note/an5698-adapting-the-xcubestl-functional-safety-package-for-stm32-iec-61508-compliant-to-other-safety-standards-stmicroelectronics.pdf
Application Notes for related Tools & Software | https://www.st.com/resource/en/application_note/an5731-stm32cubemx-and-stm32cubeide-threadsafe-solution-stmicroelectronics.pdf
Application Notes for related Tools & Software | https://www.st.com/resource/en/application_note/an4502-stm32-smbuspmbus-expansion-package-for-stm32cube-stmicroelectronics.pdf
Application Notes for related Tools & Software | https://www.st.com/resource/en/application_note/an5952-how-to-use-cmake-in-stm32cubeide-stmicroelectronics.pdf
Errata Sheets | https://www.st.com/resource/en/errata_sheet/es0298-stm32f446xcxe-device-limitations-stmicroelectronics.pdf
Datasheet | https://www.st.com/resource/en/datasheet/dm00141306.pdf
Programming Manuals | https://www.st.com/resource/en/programming_manual/pm0214-stm32-cortexm4-mcus-and-mpus-programming-manual-stmicroelectronics.pdf
Reference Manuals | https://www.st.com/resource/en/reference_manual/rm0390-stm32f446xx-advanced-armbased-32bit-mcus-stmicroelectronics.pdf
Technical Notes & Articles | https://www.st.com/resource/en/technical_note/tn0516-overview-of-the-stm32f0xf100xxf103xx-and-stm32f2xxf30xf4xx-mcus-pmsm-singledual-foc-sdk-v40-stmicroelectronics.pdf

Technical Notes & Articles | https://www.st.com/resource/en/technical_note/tn1163-description-of-wlcsp-for-microcontrollers-and-recommendations-for-its-use-stmicroelectronics.pdf
Technical Notes & Articles | https://www.st.com/resource/en/technical_note/tn1204-tape-and-reel-shipping-media-for-stm32-microcontrollers-in-bga-packages-stmicroelectronics.pdf
Technical Notes & Articles | https://www.st.com/resource/en/technical_note/tn1205-tape-and-reel-shipping-media-for-stm8-and-stm32-microcontrollers-in-fpn-packages-stmicroelectronics.pdf
Technical Notes & Articles | https://www.st.com/resource/en/technical_note/tn1206-tape-and-reel-shipping-media-for-stm8-and-stm32-microcontrollers-in-qfp-packages-stmicroelectronics.pdf
Technical Notes & Articles | https://www.st.com/resource/en/technical_note/tn1207-tape-and-reel-shipping-media-for-stm8-and-stm32-microcontrollers-in-so-packages-stmicroelectronics.pdf
Technical Notes & Articles | https://www.st.com/resource/en/technical_note/tn1208-tape-and-reel-shipping-media-for-stm8-and-stm32-microcontrollers-in-tssop-and-ssop-packages-stmicroelectronics.pdf
Technical Notes & Articles | https://www.st.com/resource/en/technical_note/tn1433-reference-device-marking-schematics-for-stm32-microcontrollers-and-microprocessors-stmicroelectronics.pdf

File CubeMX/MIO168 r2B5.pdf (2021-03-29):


29/03/2021

## MIO168 r2B5 Project Configuration Report

# 1. Description

## 1.1. Project

Project Name | MIO168 r2B5
Board Name | custom
Generated with: | STM32CubeMX 6.2.0
Date | 03/29/2021

## 1.2. MCU

MCU Series | STM32F4
MCU Line | STM32F446
MCU name | STM32F446ZCTx
MCU Package | LQFP144
MCU Pin number | 144

## 1.3. Core(s) information

Core(s) | Arm Cortex-M4

# 2. Pinout Configuration

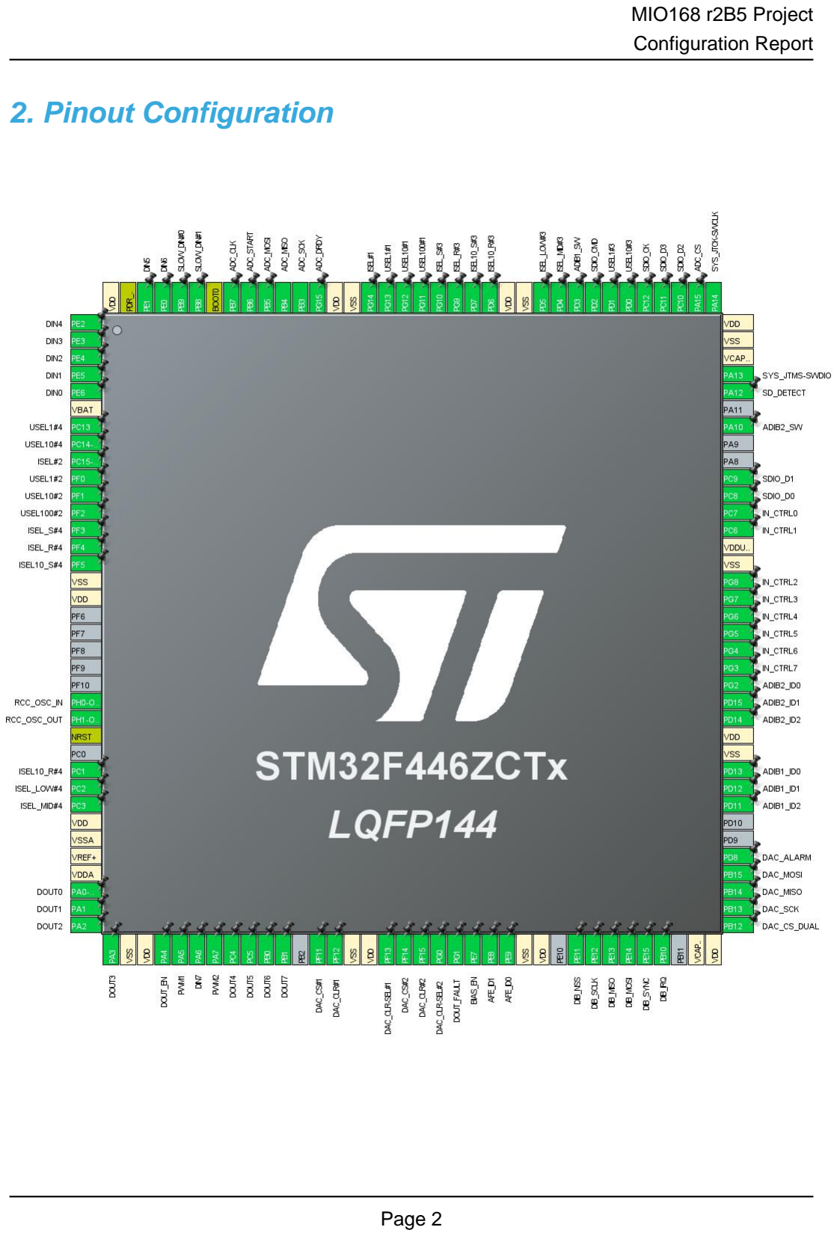
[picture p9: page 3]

# 3. Pins Configuration

Pin Number LQFP144 | Pin Name (function after reset) | Pin Type | Alternate Function(s) | Label
1 | PE2 * | I/O | GPIO_Input | DIN4
2 | PE3 * | I/O | GPIO_Input | DIN3
3 | PE4 * | I/O | GPIO_Input | DIN2
4 | PE5 | I/O | TIM9_CH1 | DIN1
5 | PE6 | I/O | TIM9_CH2 | DIN0
6 | VBAT | Power
7 | PC13 * | I/O | GPIO_Output | USEL1#4
8 | PC14-OSC32_IN * | I/O | GPIO_Output | USEL10#4
9 | PC15-OSC32_OUT * | I/O | GPIO_Output | ISEL#2
10 | PF0 * | I/O | GPIO_Output | USEL1#2
11 | PF1 * | I/O | GPIO_Output | USEL10#2
12 | PF2 * | I/O | GPIO_Output | USEL100#2
13 | PF3 * | I/O | GPIO_Output | ISEL_S#4
14 | PF4 * | I/O | GPIO_Output | ISEL_R#4
15 | PF5 * | I/O | GPIO_Output | ISEL10_S#4
16 | VSS | Power
17 | VDD | Power
23 | PH0-OSC_IN | I/O | RCC_OSC_IN
24 | PH1-OSC_OUT | I/O | RCC_OSC_OUT
25 | NRST | Reset
27 | PC1 * | I/O | GPIO_Output | ISEL10_R#4
28 | PC2 * | I/O | GPIO_Output | ISEL_LOW#4
29 | PC3 * | I/O | GPIO_Output | ISEL_MID#4
30 | VDD | Power
31 | VSSA | Power
32 | VREF+ | Power
33 | VDDA | Power
34 | PA0-WKUP * | I/O | GPIO_Output | DOUT0
35 | PA1 * | I/O | GPIO_Output | DOUT1
36 | PA2 * | I/O | GPIO_Output | DOUT2
37 | PA3 * | I/O | GPIO_Output | DOUT3
38 | VSS | Power
39 | VDD | Power
40 | PA4 * | I/O | GPIO_Output | DOUT_EN
41 | PA5 | I/O | TIM2_CH1 | PWM1
42 | PA6 * | I/O | GPIO_Input | DIN7

Pin Number LQFP144 | Pin Name (function after reset) | Pin Type | Alternate Function(s) | Label
43 | PA7 | I/O | TIM3_CH2 | PWM2
44 | PC4 * | I/O | GPIO_Output | DOUT4
45 | PC5 * | I/O | GPIO_Output | DOUT5
46 | PB0 * | I/O | GPIO_Output | DOUT6
47 | PB1 * | I/O | GPIO_Output | DOUT7
49 | PF11 * | I/O | GPIO_Output | DAC_CS#1
50 | PF12 * | I/O | GPIO_Output | DAC_CLR#1
51 | VSS | Power
52 | VDD | Power
53 | PF13 * | I/O | GPIO_Output | DAC_CLR-SEL#1
54 | PF14 * | I/O | GPIO_Output | DAC_CS#2
55 | PF15 * | I/O | GPIO_Output | DAC_CLR#2
56 | PG0 | I/O | GPIO_EXTI0 | DAC_CLR-SEL#2
57 | PG1 * | I/O | GPIO_Input | DOUT_FAULT
58 | PE7 * | I/O | GPIO_Output | BIAS_EN
59 | PE8 * | I/O | GPIO_Input | AFE_ID1
60 | PE9 * | I/O | GPIO_Input | AFE_ID0
61 | VSS | Power
62 | VDD | Power
64 | PE11 | I/O | SPI4_NSS | DIB_NSS
65 | PE12 | I/O | SPI4_SCK | DIB_SCLK
66 | PE13 | I/O | SPI4_MISO | DIB_MISO
67 | PE14 | I/O | SPI4_MOSI | DIB_MOSI
68 | PE15 * | I/O | GPIO_Input | DIB_SYNC
69 | PB10 * | I/O | GPIO_Output | DIB_IRQ
71 | VCAP_1 | Power
72 | VDD | Power
73 | PB12 * | I/O | GPIO_Output | DAC_CS_DUAL
74 | PB13 | I/O | SPI2_SCK | DAC_SCK
75 | PB14 | I/O | SPI2_MISO | DAC_MISO
76 | PB15 | I/O | SPI2_MOSI | DAC_MOSI
77 | PD8 | I/O | GPIO_EXTI8 | DAC_ALARM
80 | PD11 * | I/O | GPIO_Input | ADIB1_ID2
81 | PD12 * | I/O | GPIO_Input | ADIB1_ID1
82 | PD13 * | I/O | GPIO_Input | ADIB1_ID0
83 | VSS | Power
84 | VDD | Power
85 | PD14 * | I/O | GPIO_Input | ADIB2_ID2
86 | PD15 * | I/O | GPIO_Input | ADIB2_ID1

Pin Number LQFP144 | Pin Name (function after reset) | Pin Type | Alternate Function(s) | Label
87 | PG2 * | I/O | GPIO_Input | ADIB2_ID0
88 | PG3 * | I/O | GPIO_Output | IN_CTRL7
89 | PG4 * | I/O | GPIO_Output | IN_CTRL6
90 | PG5 * | I/O | GPIO_Output | IN_CTRL5
91 | PG6 * | I/O | GPIO_Output | IN_CTRL4
92 | PG7 * | I/O | GPIO_Output | IN_CTRL3
93 | PG8 * | I/O | GPIO_Output | IN_CTRL2
94 | VSS | Power
95 | VDDUSB | Power
96 | PC6 * | I/O | GPIO_Output | IN_CTRL1
97 | PC7 * | I/O | GPIO_Output | IN_CTRL0
98 | PC8 | I/O | SDIO_D0
99 | PC9 | I/O | SDIO_D1
102 | PA10 * | I/O | GPIO_Output | ADIB2_SW
104 | PA12 * | I/O | GPIO_Input | SD_DETECT
105 | PA13 | I/O | SYS_JTMS-SWDIO
106 | VCAP_2 | Power
107 | VSS | Power
108 | VDD | Power
109 | PA14 | I/O | SYS_JTCK-SWCLK
110 | PA15 * | I/O | GPIO_Output | ADC_CS
111 | PC10 | I/O | SDIO_D2
112 | PC11 | I/O | SDIO_D3
113 | PC12 | I/O | SDIO_CK
114 | PD0 * | I/O | GPIO_Output | USEL10#3
115 | PD1 * | I/O | GPIO_Output | USEL1#3
116 | PD2 | I/O | SDIO_CMD
117 | PD3 * | I/O | GPIO_Output | ADIB1_SW
118 | PD4 * | I/O | GPIO_Output | ISEL_MID#3
119 | PD5 * | I/O | GPIO_Output | ISEL_LOW#3
120 | VSS | Power
121 | VDD | Power
122 | PD6 * | I/O | GPIO_Output | ISEL10_R#3
123 | PD7 * | I/O | GPIO_Output | ISEL10_S#3
124 | PG9 * | I/O | GPIO_Output | ISEL_R#3
125 | PG10 * | I/O | GPIO_Output | ISEL_S#3
126 | PG11 * | I/O | GPIO_Output | USEL100#1
127 | PG12 * | I/O | GPIO_Output | USEL10#1
128 | PG13 * | I/O | GPIO_Output | USEL1#1

Pin Number LQFP144 | Pin Name (function after reset) | Pin Type | Alternate Function(s) | Label
129 | PG14 * | I/O | GPIO_Output | ISEL#1
130 | VSS | Power
131 | VDD | Power
132 | PG15 | I/O | GPIO_EXTI15 | ADC_DRDY
133 | PB3 | I/O | SPI3_SCK | ADC_SCK
134 | PB4 | I/O | SPI3_MISO | ADC_MISO
135 | PB5 | I/O | SPI3_MOSI | ADC_MOSI
136 | PB6 * | I/O | GPIO_Output | ADC_START
137 | PB7 * | I/O | GPIO_Output | ADC_CLK
138 | BOOT0 | Boot
139 | PB8 * | I/O | GPIO_Output | SLOW_DIN#1
140 | PB9 * | I/O | GPIO_Output | SLOW_DIN#0
141 | PE0 * | I/O | GPIO_Input | DIN6
142 | PE1 * | I/O | GPIO_Input | DIN5
143 | PDR_ON | Reset
144 | VDD | Power

## * The pin is affected with an I/O function

# 4. Clock Tree Configuration

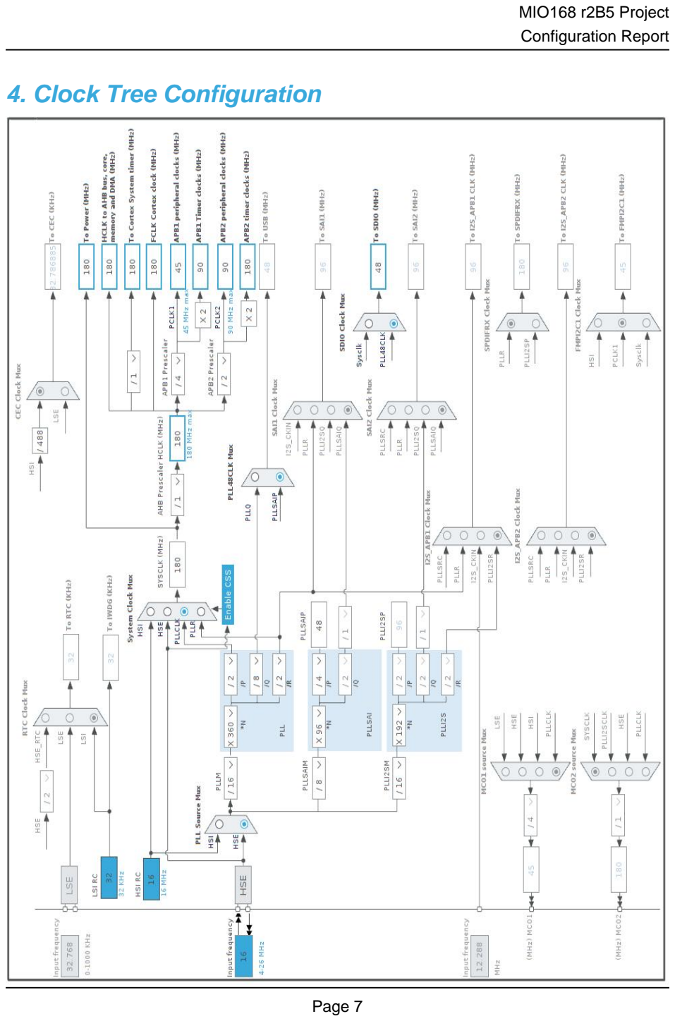
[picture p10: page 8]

# 5. Software Project

## 5.1. Project Settings

Name | Value
Project Name | MIO168 r2B5
Project Folder | /home/denis/BACKUP/EEZ/git-public/dib-mio168/CubeMX
Toolchain / IDE | STM32CubeIDE
Firmware Package Name and Version | STM32Cube FW_F4 V1.26.0
Application Structure | Advanced
Generate Under Root | Yes
Do not generate the main() | No
Minimum Heap Size | 0x2000
Minimum Stack Size | 0x4000

## 5.2. Code Generation Settings

Name | Value
STM32Cube MCU packages and embedded software | Copy only the necessary library files
Generate peripheral initialization as a pair of '.c/.h' files | No
Backup previously generated files when re-generating | No
Keep User Code when re-generating | Yes
Delete previously generated files when not re-generated | Yes
Set all free pins as analog (to optimize the power consumption) | No
Enable Full Assert | No

## 5.3. Advanced Settings - Generated Function Calls

Rank | Function Name | Peripheral Instance Name
1 | MX_GPIO_Init | GPIO
2 | MX_DMA_Init | DMA
3 | SystemClock_Config | RCC
4 | MX_SDIO_SD_Init | SDIO
5 | MX_SPI4_Init | SPI4
6 | MX_CRC_Init | CRC
7 | MX_SPI2_Init | SPI2
8 | MX_SPI3_Init | SPI3
9 | MX_TIM9_Init | TIM9
10 | MX_FATFS_Init | FATFS
11 | MX_TIM6_Init | TIM6

Rank | Function Name | Peripheral Instance Name
12 | MX_TIM2_Init | TIM2
13 | MX_TIM3_Init | TIM3

# 6. Power Consumption Calculator report

## 6.1. Microcontroller Selection

Series | STM32F4
Line | STM32F446
MCU | STM32F446ZCTx
Datasheet | DS10693_Rev6

## 6.2. Parameter Selection

Temperature | 25
Vdd | 3.3

## 6.3. Battery Selection

Battery | Li-SOCL2(A3400)
Capacity | 3400.0 mAh
Self Discharge | 0.08 %/month
Nominal Voltage | 3.6 V
Max Cont Current | 100.0 mA
Max Pulse Current | 200.0 mA
Cells in series | 1
Cells in parallel | 1

## 6.4. Sequence

Step | Step1 | Step2
Mode | RUN | STOP_UDM (Under Drive)
Vdd | 3.3 | 3.3
Voltage Source | Battery | Battery
Range | Scale1-High | No Scale
Fetch Type | RAM/FLASH/REGON/ART/P REFETCH | n/a
CPU Frequency | 180 MHz | 0 Hz
Clock Configuration | HSE PLL | Regulator_LP Flash-PwrDwn
Clock Source Frequency | 4 MHz | 0 Hz

### Peripherals

Additional Cons. | 0 mA | 0 mA
Average Current | 46 mA | 55 µA
Duration | 0.1 ms | 0.9 ms
DMIPS | 225.0 | 0.0
Ta Max | 99.99 | 104.99
Category | In DS Table | In DS Table

## 6.5. Results

Sequence Time | 1 ms | Average Current | 4.65 mA
Battery Life | 1 month | Average DMIPS | 225.0 DMIPS

## 6.6. Chart

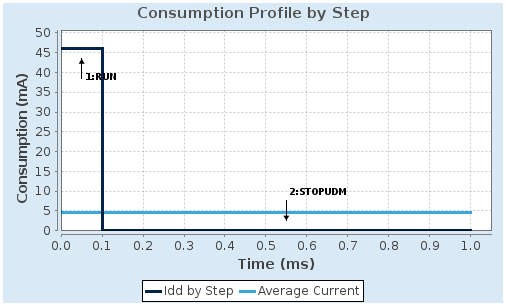
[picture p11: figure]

# 7. Peripherals and Middlewares Configuration

## 7.1. CRC mode: Activated

## 7.2. RCC High Speed Clock (HSE): Crystal/Ceramic Resonator

## 7.2.1. Parameter Settings:

### System Parameters:

VDD voltage (V) | 3.3
Instruction Cache | Enabled
Prefetch Buffer | Enabled
Data Cache | Enabled
Flash Latency(WS) | 5 WS (6 CPU cycle)

### RCC Parameters:

HSI Calibration Value | 16
TIM Prescaler Selection | Disabled
HSE Startup Timout Value (ms) | 100
LSE Startup Timout Value (ms) | 5000

### Power Parameters:

Power Regulator Voltage Scale | Power Regulator Voltage Scale 1
Power Over Drive | Enabled

## 7.3. SDIO Mode: SD 4 bits Wide bus

## 7.3.1. Parameter Settings:

### SDIO parameters:

Clock transition on which the bit capture is made | Rising transition
SDIO Clock divider bypass | Enable *
SDIO Clock output enable when the bus is idle | Disable the power save for the clock
SDIO hardware flow control | The hardware control flow is enabled *
SDIOCLK clock divide factor | 3 *

## 7.4. SPI2 Mode: Full-Duplex Master

## 7.4.1. Parameter Settings:

### Basic Parameters:

Frame Format | Motorola
Data Size | 8 Bits
First Bit | MSB First

### Clock Parameters:

Prescaler (for Baud Rate) | 4 *
Baud Rate | 11.25 MBits/s *
Clock Polarity (CPOL) | Low
Clock Phase (CPHA) | 1 Edge

### Advanced Parameters:

CRC Calculation | Disabled
NSS Signal Type | Software

## 7.5. SPI3 Mode: Full-Duplex Master

## 7.5.1. Parameter Settings:

### Basic Parameters:

Frame Format | Motorola
Data Size | 8 Bits
First Bit | MSB First

### Clock Parameters:

Prescaler (for Baud Rate) | 4 *
Baud Rate | 11.25 MBits/s *
Clock Polarity (CPOL) | Low
Clock Phase (CPHA) | 2 Edge *

### Advanced Parameters:

CRC Calculation | Disabled
NSS Signal Type | Software

## 7.6. SPI4

## Mode: Full-Duplex Slave Hardware NSS Signal: Hardware NSS Input Signal

## 7.6.1. Parameter Settings:

### Basic Parameters:

Frame Format | Motorola
Data Size | 8 Bits
First Bit | MSB First

### Clock Parameters:

Clock Polarity (CPOL) | Low
Clock Phase (CPHA) | 1 Edge

### Advanced Parameters:

CRC Calculation | Enabled *
CRC Polynomial | X0+X1+X2 *
NSS Signal Type | Input Hardware

## 7.7. SYS Debug: Serial Wire Timebase Source: SysTick

## 7.8. TIM2 Channel1: PWM Generation CH1

## 7.8.1. Parameter Settings:

### Counter Settings:

Prescaler (PSC - 16 bits value) | 0
Counter Mode | Up
Counter Period (AutoReload Register - 32 bits value ) | 0 *
Internal Clock Division (CKD) | No Division
auto-reload preload | Disable

### Trigger Output (TRGO) Parameters:

Master/Slave Mode (MSM bit) | Disable (Trigger input effect not delayed)
Trigger Event Selection | Reset (UG bit from TIMx_EGR)

### PWM Generation Channel 1:

Mode | PWM mode 1
Pulse (32 bits value) | 0
Output compare preload | Enable

Fast Mode | Disable
CH Polarity | High

## 7.9. TIM3 Channel2: PWM Generation CH2

## 7.9.1. Parameter Settings:

### Counter Settings:

Prescaler (PSC - 16 bits value) | 0
Counter Mode | Up
Counter Period (AutoReload Register - 16 bits value ) | 0 *
Internal Clock Division (CKD) | No Division
auto-reload preload | Disable

### Trigger Output (TRGO) Parameters:

Master/Slave Mode (MSM bit) | Disable (Trigger input effect not delayed)
Trigger Event Selection | Reset (UG bit from TIMx_EGR)

### PWM Generation Channel 2:

Mode | PWM mode 1
Pulse (16 bits value) | 0
Output compare preload | Enable
Fast Mode | Disable
CH Polarity | High

## 7.10. TIM6 mode: Activated

## 7.10.1. Parameter Settings:

### Counter Settings:

Prescaler (PSC - 16 bits value) | 8 *
Counter Mode | Up
Counter Period (AutoReload Register - 16 bits value ) | 999 *
auto-reload preload | Enable *

### Trigger Output (TRGO) Parameters:

Trigger Event Selection | Reset (UG bit from TIMx_EGR)

## 7.11. TIM9 Channel1: Input Capture direct mode Channel2: Input Capture direct mode

## 7.11.1. Parameter Settings:

### Counter Settings:

Prescaler (PSC - 16 bits value) | 0
Counter Mode | Up
Counter Period (AutoReload Register - 16 bits value ) | 0 *
Internal Clock Division (CKD) | No Division
auto-reload preload | Disable

### Input Capture Channel 1:

Polarity Selection | Rising Edge
IC Selection | Direct
Prescaler Division Ratio | No division
Input Filter (4 bits value) | 0

### Input Capture Channel 2:

Polarity Selection | Rising Edge
IC Selection | Direct
Prescaler Division Ratio | No division
Input Filter (4 bits value) | 0

## 7.12. FATFS mode: SD Card

## 7.12.1. Set Defines:

### Version:

FATFS version | R0.12c

### Function Parameters:

FS_READONLY (Read-only mode) | Disabled
FS_MINIMIZE (Minimization level) | Disabled
USE_STRFUNC (String functions) | Enabled with LF -> CRLF conversion
USE_FIND (Find functions) | Disabled
USE_MKFS (Make filesystem function) | Enabled
USE_FASTSEEK (Fast seek function) | Enabled
USE_EXPAND (Use f_expand function) | Disabled
USE_CHMOD (Change attributes function) | Disabled

USE_LABEL (Volume label functions) | Disabled
USE_FORWARD (Forward function) | Disabled

### Locale and Namespace Parameters:

CODE_PAGE (Code page on target) | Latin 1
USE_LFN (Use Long Filename) | Enabled with dynamic working buffer on the STACK *
MAX_LFN (Max Long Filename) | 255
LFN_UNICODE (Enable Unicode) | ANSI/OEM
STRF_ENCODE (Character encoding) | UTF-8
FS_RPATH (Relative Path) | Disabled

### Physical Drive Parameters:

VOLUMES (Logical drives) | 1
MAX_SS (Maximum Sector Size) | 512
MIN_SS (Minimum Sector Size) | 512
MULTI_PARTITION (Volume partitions feature) | Disabled
USE_TRIM (Erase feature) | Disabled
FS_NOFSINFO (Force full FAT scan) | 0

### System Parameters:

FS_TINY (Tiny mode) | Disabled
FS_EXFAT (Support of exFAT file system) | Disabled
FS_NORTC (Timestamp feature) | Dynamic timestamp
FS_REENTRANT (Re-Entrancy) | Disabled
FS_TIMEOUT (Timeout ticks) | 1000
FS_LOCK (Number of files opened simultaneously) | 2

## 7.12.2. Advanced Settings:

### SDIO/SDMMC:

SDIO instance | SDIO
Use dma template | Disabled
BSP code for SD | Generic

## 7.12.3. Platform Settings:

Detect_SDIO | PA12

### * User modified value

# 8. System Configuration

## 8.1. GPIO configuration

IP | Pin | Signal | GPIO mode | GPIO pull/up pull down

## Max Speed

## User Label

RCC | PH0- OSC_IN | RCC_OSC_IN | n/a | n/a | n/a
| PH1- OSC_OUT | RCC_OSC_OUT | n/a | n/a | n/a
SDIO | PC8 | SDIO_D0 | Alternate Function Push Pull | No pull-up and no pull-down | Very High
| PC9 | SDIO_D1 | Alternate Function Push Pull | No pull-up and no pull-down | Very High
| PC10 | SDIO_D2 | Alternate Function Push Pull | No pull-up and no pull-down | Very High
| PC11 | SDIO_D3 | Alternate Function Push Pull | No pull-up and no pull-down | Very High
| PC12 | SDIO_CK | Alternate Function Push Pull | No pull-up and no pull-down | Very High
| PD2 | SDIO_CMD | Alternate Function Push Pull | No pull-up and no pull-down | Very High
SPI2 | PB13 | SPI2_SCK | Alternate Function Push Pull | No pull-up and no pull-down | Very High
*
| | | | | | DAC_SCK
| PB14 | SPI2_MISO | Alternate Function Push Pull | No pull-up and no pull-down | Very High
*
| | | | | | DAC_MISO
| PB15 | SPI2_MOSI | Alternate Function Push Pull | No pull-up and no pull-down | Very High
*
| | | | | | DAC_MOSI
SPI3 | PB3 | SPI3_SCK | Alternate Function Push Pull | No pull-up and no pull-down | Very High
*
| | | | | | ADC_SCK
| PB4 | SPI3_MISO | Alternate Function Push Pull | No pull-up and no pull-down | Very High
*
| | | | | | ADC_MISO
| PB5 | SPI3_MOSI | Alternate Function Push Pull | No pull-up and no pull-down | Very High
*
| | | | | | ADC_MOSI
SPI4 | PE11 | SPI4_NSS | Alternate Function Push Pull | No pull-up and no pull-down | Very High
*
| | | | | | DIB_NSS
| PE12 | SPI4_SCK | Alternate Function Push Pull | No pull-up and no pull-down | Very High
*
| | | | | | DIB_SCLK
| PE13 | SPI4_MISO | Alternate Function Push Pull | No pull-up and no pull-down | Very High
*
| | | | | | DIB_MISO
| PE14 | SPI4_MOSI | Alternate Function Push Pull | No pull-up and no pull-down | Very High
*
| | | | | | DIB_MOSI
SYS | PA13 | SYS_JTMS- SWDIO | n/a | n/a | n/a
| PA14 | SYS_JTCK- SWCLK | n/a | n/a | n/a
TIM2 | PA5 | TIM2_CH1 | Alternate Function Push Pull | No pull-up and no pull-down | Low | PWM1

IP | Pin | Signal | GPIO mode | GPIO pull/up pull down | Max Speed | User Label
TIM3 | PA7 | TIM3_CH2 | Alternate Function Push Pull | No pull-up and no pull-down | Low | PWM2
TIM9 | PE5 | TIM9_CH1 | Alternate Function Push Pull | No pull-up and no pull-down | Low | DIN1
| PE6 | TIM9_CH2 | Alternate Function Push Pull | No pull-up and no pull-down | Low | DIN0
GPIO | PE2 | GPIO_Input | Input mode | No pull-up and no pull-down | n/a | DIN4
PE3 | GPIO_Input | Input mode | No pull-up and no pull-down | n/a | DIN3
PE4 | GPIO_Input | Input mode | No pull-up and no pull-down | n/a | DIN2
PC13 | GPIO_Output | Output Push Pull | No pull-up and no pull-down | Low | USEL1#4
PC14-OSC32_IN | GPIO_Output | Output Push Pull | No pull-up and no pull-down | Low | USEL10#4
PC15-OSC32_OU T | GPIO_Output | Output Push Pull | No pull-up and no pull-down | Low | ISEL#2
PF0 | GPIO_Output | Output Push Pull | No pull-up and no pull-down | Low | USEL1#2
PF1 | GPIO_Output | Output Push Pull | No pull-up and no pull-down | Low | USEL10#2
PF2 | GPIO_Output | Output Push Pull | No pull-up and no pull-down | Low | USEL100#2
PF3 | GPIO_Output | Output Push Pull | No pull-up and no pull-down | Low | ISEL_S#4
PF4 | GPIO_Output | Output Push Pull | No pull-up and no pull-down | Low | ISEL_R#4
PF5 | GPIO_Output | Output Push Pull | No pull-up and no pull-down | Low | ISEL10_S#4
PC1 | GPIO_Output | Output Push Pull | No pull-up and no pull-down | Low | ISEL10_R#4
PC2 | GPIO_Output | Output Push Pull | No pull-up and no pull-down | Low | ISEL_LOW#4
PC3 | GPIO_Output | Output Push Pull | No pull-up and no pull-down | Low | ISEL_MID#4
PA0-WKUP | GPIO_Output | Output Push Pull | No pull-up and no pull-down | Low | DOUT0
PA1 | GPIO_Output | Output Push Pull | No pull-up and no pull-down | Low | DOUT1
PA2 | GPIO_Output | Output Push Pull | No pull-up and no pull-down | Low | DOUT2
PA3 | GPIO_Output | Output Push Pull | No pull-up and no pull-down | Low | DOUT3
PA4 | GPIO_Output | Output Push Pull | No pull-up and no pull-down | Low | DOUT_EN
PA6 | GPIO_Input | Input mode | No pull-up and no pull-down | n/a | DIN7
PC4 | GPIO_Output | Output Push Pull | No pull-up and no pull-down | Low | DOUT4
PC5 | GPIO_Output | Output Push Pull | No pull-up and no pull-down | Low | DOUT5
PB0 | GPIO_Output | Output Push Pull | No pull-up and no pull-down | Low | DOUT6
PB1 | GPIO_Output | Output Push Pull | No pull-up and no pull-down | Low | DOUT7
PF11 | GPIO_Output | Output Push Pull | No pull-up and no pull-down | Low | DAC_CS#1
PF12 | GPIO_Output | Output Push Pull | No pull-up and no pull-down | Low | DAC_CLR#1
PF13 | GPIO_Output | Output Push Pull | No pull-up and no pull-down | Very High * | DAC_CLR-SEL#1
PF14 | GPIO_Output | Output Push Pull | No pull-up and no pull-down | Low | DAC_CS#2
PF15 | GPIO_Output | Output Push Pull | No pull-up and no pull-down | Low | DAC_CLR#2
PG0 | GPIO_EXTI0 | External Interrupt Mode with Rising edge trigger detection | Pull-up * | n/a | DAC_CLR-SEL#2
PG1 | GPIO_Input | Input mode | Pull-up * | n/a | DOUT_FAULT
PE7 | GPIO_Output | Output Push Pull | No pull-up and no pull-down | Low | BIAS_EN

IP | Pin | Signal | GPIO mode | GPIO pull/up pull down

## Max Speed

## User Label

PE8 | GPIO_Input | Input mode | Pull-up * | n/a | AFE_ID1
PE9 | GPIO_Input | Input mode | Pull-up * | n/a | AFE_ID0
PE15 | GPIO_Input | Input mode | No pull-up and no pull-down | n/a | DIB_SYNC
PB10 | GPIO_Output | Output Push Pull | No pull-up and no pull-down | Low | DIB_IRQ
PB12 | GPIO_Output | Output Push Pull | No pull-up and no pull-down | Low | DAC_CS_DUAL
PD8 | GPIO_EXTI8 | External Interrupt Mode with Rising edge trigger detection | Pull-up * | n/a | DAC_ALARM
PD11 | GPIO_Input | Input mode | Pull-up * | n/a | ADIB1_ID2
PD12 | GPIO_Input | Input mode | Pull-up * | n/a | ADIB1_ID1
PD13 | GPIO_Input | Input mode | Pull-up * | n/a | ADIB1_ID0
PD14 | GPIO_Input | Input mode | Pull-up * | n/a | ADIB2_ID2
PD15 | GPIO_Input | Input mode | Pull-up * | n/a | ADIB2_ID1
PG2 | GPIO_Input | Input mode | Pull-up * | n/a | ADIB2_ID0
PG3 | GPIO_Output | Output Push Pull | No pull-up and no pull-down | Low | IN_CTRL7
PG4 | GPIO_Output | Output Push Pull | No pull-up and no pull-down | Low | IN_CTRL6
PG5 | GPIO_Output | Output Push Pull | No pull-up and no pull-down | Low | IN_CTRL5
PG6 | GPIO_Output | Output Push Pull | No pull-up and no pull-down | Low | IN_CTRL4
PG7 | GPIO_Output | Output Push Pull | No pull-up and no pull-down | Low | IN_CTRL3
PG8 | GPIO_Output | Output Push Pull | No pull-up and no pull-down | Low | IN_CTRL2
PC6 | GPIO_Output | Output Push Pull | No pull-up and no pull-down | Low | IN_CTRL1
PC7 | GPIO_Output | Output Push Pull | No pull-up and no pull-down | Low | IN_CTRL0
PA10 | GPIO_Output | Output Push Pull | No pull-up and no pull-down | Low | ADIB2_SW
PA12 | GPIO_Input | Input mode | Pull-up * | n/a | SD_DETECT
PA15 | GPIO_Output | Output Push Pull | No pull-up and no pull-down | Low | ADC_CS
PD0 | GPIO_Output | Output Push Pull | No pull-up and no pull-down | Low | USEL10#3
PD1 | GPIO_Output | Output Push Pull | No pull-up and no pull-down | Low | USEL1#3
PD3 | GPIO_Output | Output Push Pull | No pull-up and no pull-down | Low | ADIB1_SW
PD4 | GPIO_Output | Output Push Pull | No pull-up and no pull-down | Low | ISEL_MID#3
PD5 | GPIO_Output | Output Push Pull | No pull-up and no pull-down | Low | ISEL_LOW#3
PD6 | GPIO_Output | Output Push Pull | No pull-up and no pull-down | Low | ISEL10_R#3
PD7 | GPIO_Output | Output Push Pull | No pull-up and no pull-down | Low | ISEL10_S#3
PG9 | GPIO_Output | Output Push Pull | No pull-up and no pull-down | Low | ISEL_R#3
PG10 | GPIO_Output | Output Push Pull | No pull-up and no pull-down | Low | ISEL_S#3
PG11 | GPIO_Output | Output Push Pull | No pull-up and no pull-down | Low | USEL100#1
PG12 | GPIO_Output | Output Push Pull | No pull-up and no pull-down | Low | USEL10#1
PG13 | GPIO_Output | Output Push Pull | No pull-up and no pull-down | Low | USEL1#1
PG14 | GPIO_Output | Output Push Pull | No pull-up and no pull-down | Low | ISEL#1
PG15 | GPIO_EXTI15 | External Interrupt

### Mode with Falling

| | | Pull-up * | n/a | ADC_DRDY

IP | Pin | Signal | GPIO mode | GPIO pull/up pull down | Max Speed | User Label
| | | edge trigger detection
| PB6 | GPIO_Output | Output Push Pull | No pull-up and no pull-down | Low | ADC_START
| PB7 | GPIO_Output | Output Push Pull | No pull-up and no pull-down | Low | ADC_CLK
| PB8 | GPIO_Output | Output Push Pull | No pull-up and no pull-down | Low | SLOW_DIN#1
| PB9 | GPIO_Output | Output Push Pull | No pull-up and no pull-down | Low | SLOW_DIN#0
| PE0 | GPIO_Input | Input mode | No pull-up and no pull-down | n/a | DIN6
| PE1 | GPIO_Input | Input mode | No pull-up and no pull-down | n/a | DIN5

## 8.2. DMA configuration

DMA request | Stream | Direction | Priority
SPI4_RX | DMA2_Stream0 | Peripheral To Memory | Low
SPI4_TX | DMA2_Stream1 | Memory To Peripheral | Low
SPI2_RX | DMA1_Stream3 | Peripheral To Memory | Low
SPI2_TX | DMA1_Stream4 | Memory To Peripheral | Low
SDIO_RX | DMA2_Stream3 | Peripheral To Memory | Low
SDIO_TX | DMA2_Stream6 | Memory To Peripheral | Low
SPI3_RX | DMA1_Stream0 | Peripheral To Memory | Low
SPI3_TX | DMA1_Stream5 | Memory To Peripheral | Low

## SPI4_RX: DMA2_Stream0 DMA request Settings:

Mode: | Normal
Use fifo: | Disable
Peripheral Increment: | Disable
Memory Increment: | Enable *
Peripheral Data Width: | Byte
Memory Data Width: | Byte

## SPI4_TX: DMA2_Stream1 DMA request Settings:

Mode: | Normal
Use fifo: | Disable
Peripheral Increment: | Disable
Memory Increment: | Enable *
Peripheral Data Width: | Byte
Memory Data Width: | Byte

## SPI2_RX: DMA1_Stream3 DMA request Settings:

Mode: | Circular *
Use fifo: | Disable
Peripheral Increment: | Disable
Memory Increment: | Enable *
Peripheral Data Width: | Half Word *
Memory Data Width: | Half Word *

## SPI2_TX: DMA1_Stream4 DMA request Settings:

Mode: | Circular *
Use fifo: | Disable
Peripheral Increment: | Disable
Memory Increment: | Enable *
Peripheral Data Width: | Half Word *
Memory Data Width: | Half Word *

## SDIO_RX: DMA2_Stream3 DMA request Settings:

Mode: | Peripheral Flow Control *
Use fifo: | Enable *
FIFO Threshold: | Full
Peripheral Increment: | Disable
Memory Increment: | Enable *
Peripheral Data Width: | Word *
Memory Data Width: | Word
Peripheral Burst Size: | 4 Increment *
Memory Burst Size: | 4 Increment

## SDIO_TX: DMA2_Stream6 DMA request Settings:

Mode: | Peripheral Flow Control *
Use fifo: | Enable *
FIFO Threshold: | Full
Peripheral Increment: | Disable
Memory Increment: | Enable *
Peripheral Data Width: | Word *
Memory Data Width: | Word
Peripheral Burst Size: | 4 Increment *
Memory Burst Size: | 4 Increment

## SPI3_RX: DMA1_Stream0 DMA request Settings:

Mode: | Normal
Use fifo: | Disable

Peripheral Increment: | Disable
Memory Increment: | Enable *
Peripheral Data Width: | Byte
Memory Data Width: | Byte

## SPI3_TX: DMA1_Stream5 DMA request Settings:

Mode: | Normal
Use fifo: | Disable
Peripheral Increment: | Disable
Memory Increment: | Enable *
Peripheral Data Width: | Byte
Memory Data Width: | Byte

## 8.3. NVIC configuration

## 8.3.1. NVIC

Interrupt Table | Enable | Preenmption Priority | SubPriority
Non maskable interrupt | true | 0 | 0
Hard fault interrupt | true | 0 | 0
Memory management fault | true | 0 | 0
Pre-fetch fault, memory access fault | true | 0 | 0
Undefined instruction or illegal state | true | 0 | 0
System service call via SWI instruction | true | 0 | 0
Debug monitor | true | 0 | 0
Pendable request for system service | true | 0 | 0
System tick timer | true | 0 | 0
DMA1 stream0 global interrupt | true | 0 | 0
DMA1 stream3 global interrupt | true | 0 | 0
DMA1 stream4 global interrupt | true | 0 | 0
DMA1 stream5 global interrupt | true | 0 | 0
EXTI line[15:10] interrupts | true | 0 | 0
SDIO global interrupt | true | 0 | 0
TIM6 global interrupt and DAC1, DAC2 underrun error interrupts | true | 0 | 0
DMA2 stream0 global interrupt | true | 0 | 0
DMA2 stream1 global interrupt | true | 0 | 0
DMA2 stream3 global interrupt | true | 0 | 0
DMA2 stream6 global interrupt | true | 0 | 0
PVD interrupt through EXTI line 16 | | unused
Flash global interrupt | | unused
RCC global interrupt | | unused
EXTI line 0 interrupt | | unused
EXTI line[9:5] interrupts | | unused
TIM1 break interrupt and TIM9 global interrupt | | unused
TIM2 global interrupt | | unused
TIM3 global interrupt | | unused
SPI2 global interrupt | | unused
SPI3 global interrupt | | unused
FPU global interrupt | | unused
SPI4 global interrupt | | unused

## 8.3.2. NVIC Code generation

## Enabled interrupt Table Select for init sequence ordering

| | Generate IRQ
| | handler | Call HAL handler

Enabled interrupt Table | Select for init sequence ordering | Generate IRQ handler | Call HAL handler
Non maskable interrupt | false | true | false
Hard fault interrupt | false | true | false
Memory management fault | false | true | false
Pre-fetch fault, memory access fault | false | true | false
Undefined instruction or illegal state | false | true | false
System service call via SWI instruction | false | true | false
Debug monitor | false | true | false
Pendable request for system service | false | true | false
System tick timer | false | true | true
DMA1 stream0 global interrupt | false | true | true
DMA1 stream3 global interrupt | false | true | false
DMA1 stream4 global interrupt | false | true | false
DMA1 stream5 global interrupt | false | true | true
EXTI line[15:10] interrupts | false | true | true
SDIO global interrupt | false | true | true
TIM6 global interrupt and DAC1, DAC2 underrun error interrupts | false | true | true
DMA2 stream0 global interrupt | false | true | true
DMA2 stream1 global interrupt | false | true | true
DMA2 stream3 global interrupt | false | true | true
DMA2 stream6 global interrupt | false | true | true

### * User modified value

# 9. System Views

## 9.1. Category view 9.1.1. Current

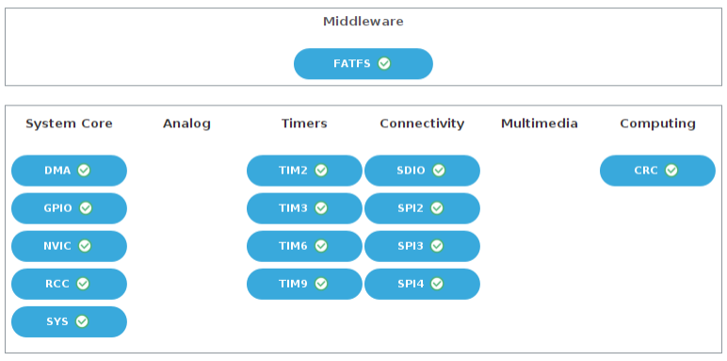
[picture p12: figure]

# 10. Docs & Resources

Type | Link
Datasheet | http://www.st.com/resource/en/datasheet/DM00141306.pdf
Reference manual | http://www.st.com/resource/en/reference_manual/DM00135183.pdf
Programming manual | http://www.st.com/resource/en/programming_manual/DM00046982.pdf
Errata sheet | http://www.st.com/resource/en/errata_sheet/DM00155929.pdf
Application note | http://www.st.com/resource/en/application_note/CD00167594.pdf
Application note | http://www.st.com/resource/en/application_note/CD00211314.pdf
Application note | http://www.st.com/resource/en/application_note/CD00249778.pdf
Application note | http://www.st.com/resource/en/application_note/CD00259245.pdf
Application note | http://www.st.com/resource/en/application_note/CD00264321.pdf
Application note | http://www.st.com/resource/en/application_note/CD00264342.pdf
Application note | http://www.st.com/resource/en/application_note/CD00264379.pdf
Application note | http://www.st.com/resource/en/application_note/DM00024853.pdf
Application note | http://www.st.com/resource/en/application_note/DM00040802.pdf
Application note | http://www.st.com/resource/en/application_note/DM00040808.pdf
Application note | http://www.st.com/resource/en/application_note/DM00042534.pdf
Application note | http://www.st.com/resource/en/application_note/DM00046011.pdf
Application note | http://www.st.com/resource/en/application_note/DM00072315.pdf
Application note | http://www.st.com/resource/en/application_note/DM00073742.pdf
Application note | http://www.st.com/resource/en/application_note/DM00073853.pdf
Application note | http://www.st.com/resource/en/application_note/DM00080497.pdf
Application note | http://www.st.com/resource/en/application_note/DM00081379.pdf
Application note | http://www.st.com/resource/en/application_note/DM00115714.pdf
Application note | http://www.st.com/resource/en/application_note/DM00129215.pdf
Application note | http://www.st.com/resource/en/application_note/DM00154959.pdf
Application note | http://www.st.com/resource/en/application_note/DM00160482.pdf

Application note | http://www.st.com/resource/en/application_note/DM00161778.pdf
Application note | http://www.st.com/resource/en/application_note/DM00213525.pdf
Application note | http://www.st.com/resource/en/application_note/DM00220769.pdf
Application note | http://www.st.com/resource/en/application_note/DM00227538.pdf
Application note | http://www.st.com/resource/en/application_note/DM00257177.pdf
Application note | http://www.st.com/resource/en/application_note/DM00272912.pdf
Application note | http://www.st.com/resource/en/application_note/DM00226326.pdf
Application note | http://www.st.com/resource/en/application_note/DM00236305.pdf
Application note | http://www.st.com/resource/en/application_note/DM00281138.pdf
Application note | http://www.st.com/resource/en/application_note/DM00296349.pdf
Application note | http://www.st.com/resource/en/application_note/DM00327191.pdf
Application note | http://www.st.com/resource/en/application_note/DM00354244.pdf
Application note | http://www.st.com/resource/en/application_note/DM00373474.pdf
Application note | http://www.st.com/resource/en/application_note/DM00315319.pdf
Application note | http://www.st.com/resource/en/application_note/DM00380469.pdf
Application note | http://www.st.com/resource/en/application_note/DM00395696.pdf
Application note | http://www.st.com/resource/en/application_note/DM00431633.pdf
Application note | http://www.st.com/resource/en/application_note/DM00493651.pdf
Application note | http://www.st.com/resource/en/application_note/DM00536349.pdf
Application note | http://www.st.com/resource/en/application_note/DM00725181.pdf

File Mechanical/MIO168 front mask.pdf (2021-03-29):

# MIO168

AI1

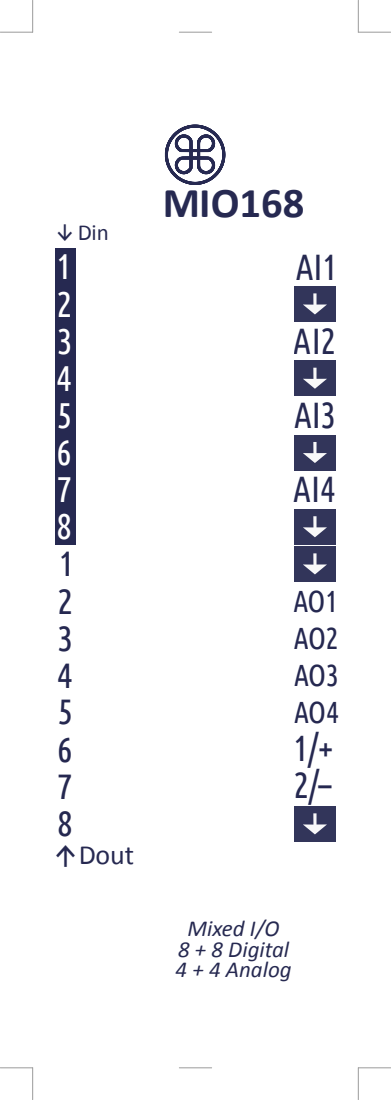
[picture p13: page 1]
Mixed I/O 8 + 8 Digital 4 + 4 Analog; U Dout; Din

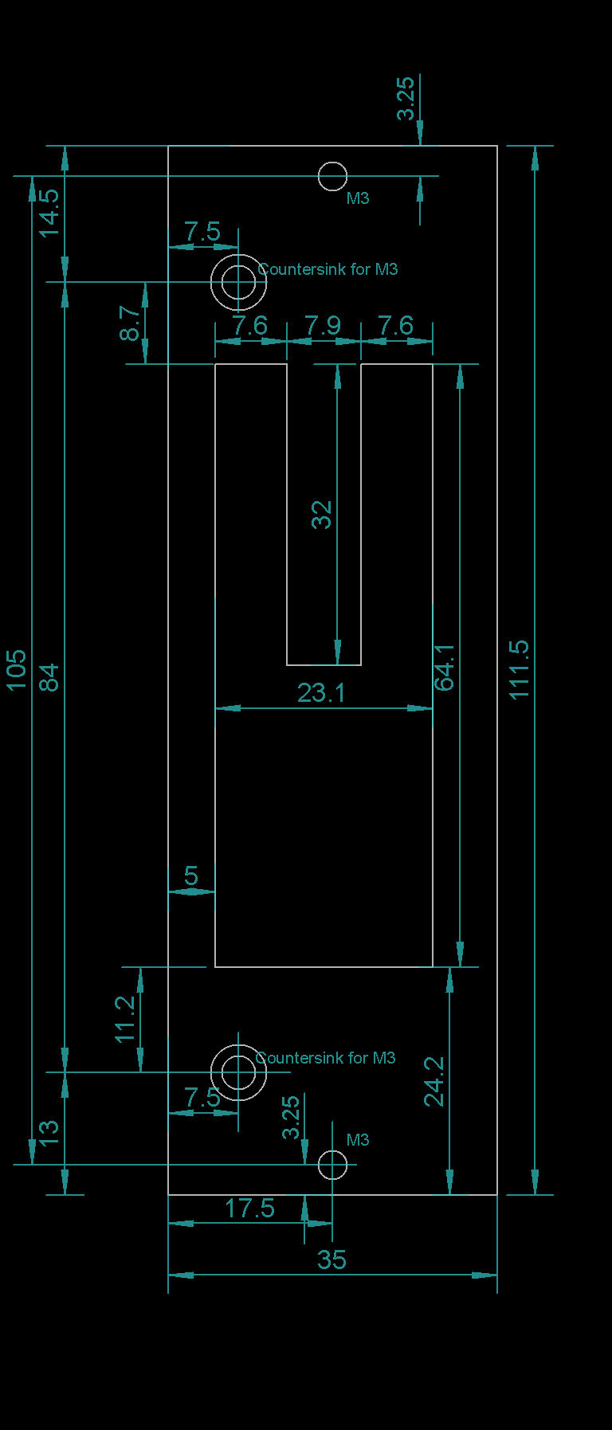
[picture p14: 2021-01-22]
Mechanical/MIO168 r2B3 front panel.png

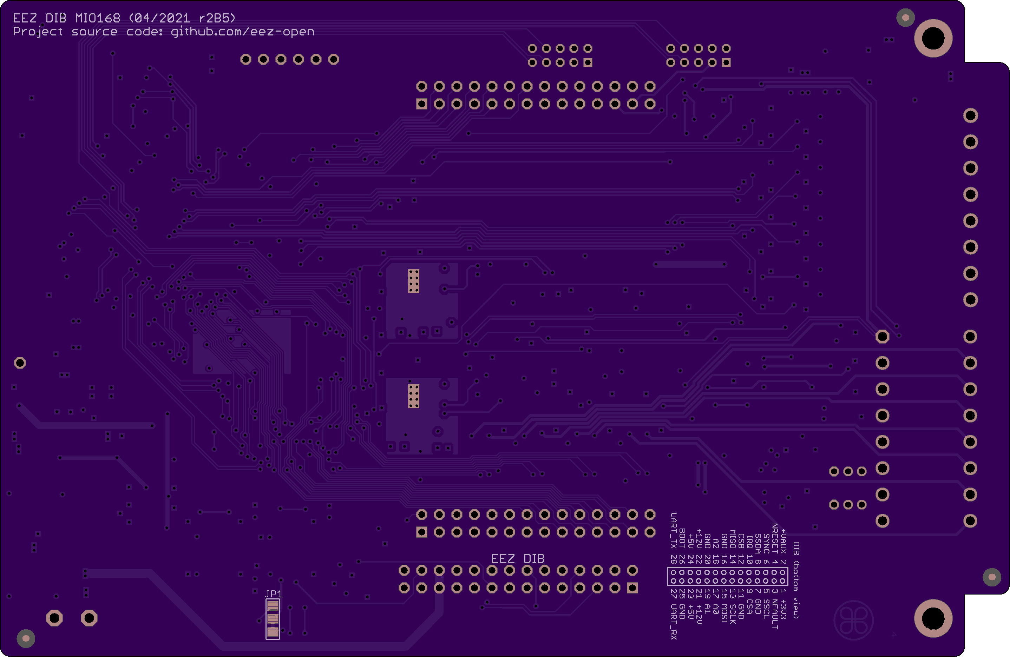
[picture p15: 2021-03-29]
Images/EEZ_DIB_MIO168_PCB_bottom.png

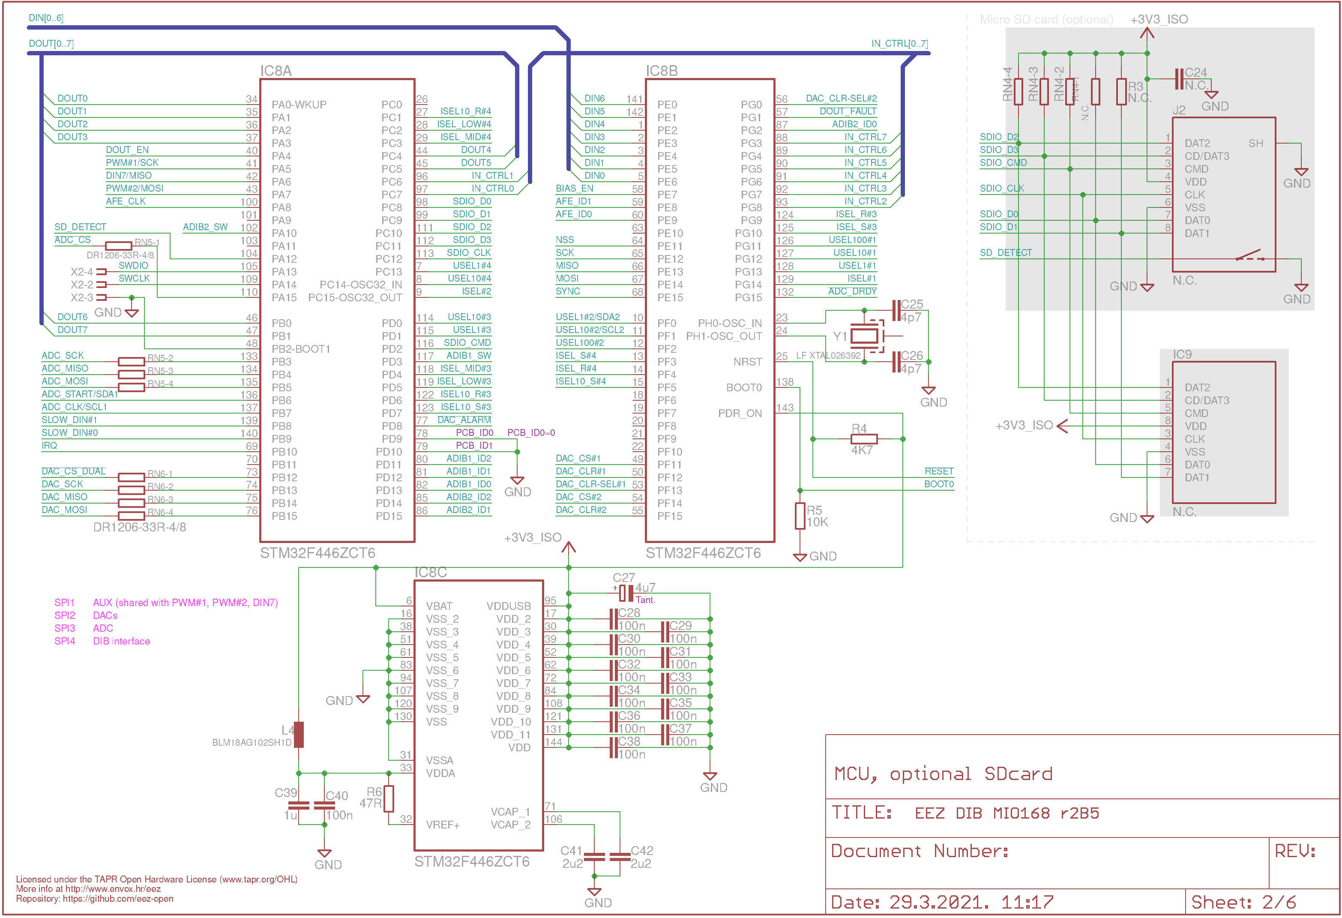
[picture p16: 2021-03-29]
EEZ DIB MIO168 r2B5 Sheet2of6.png

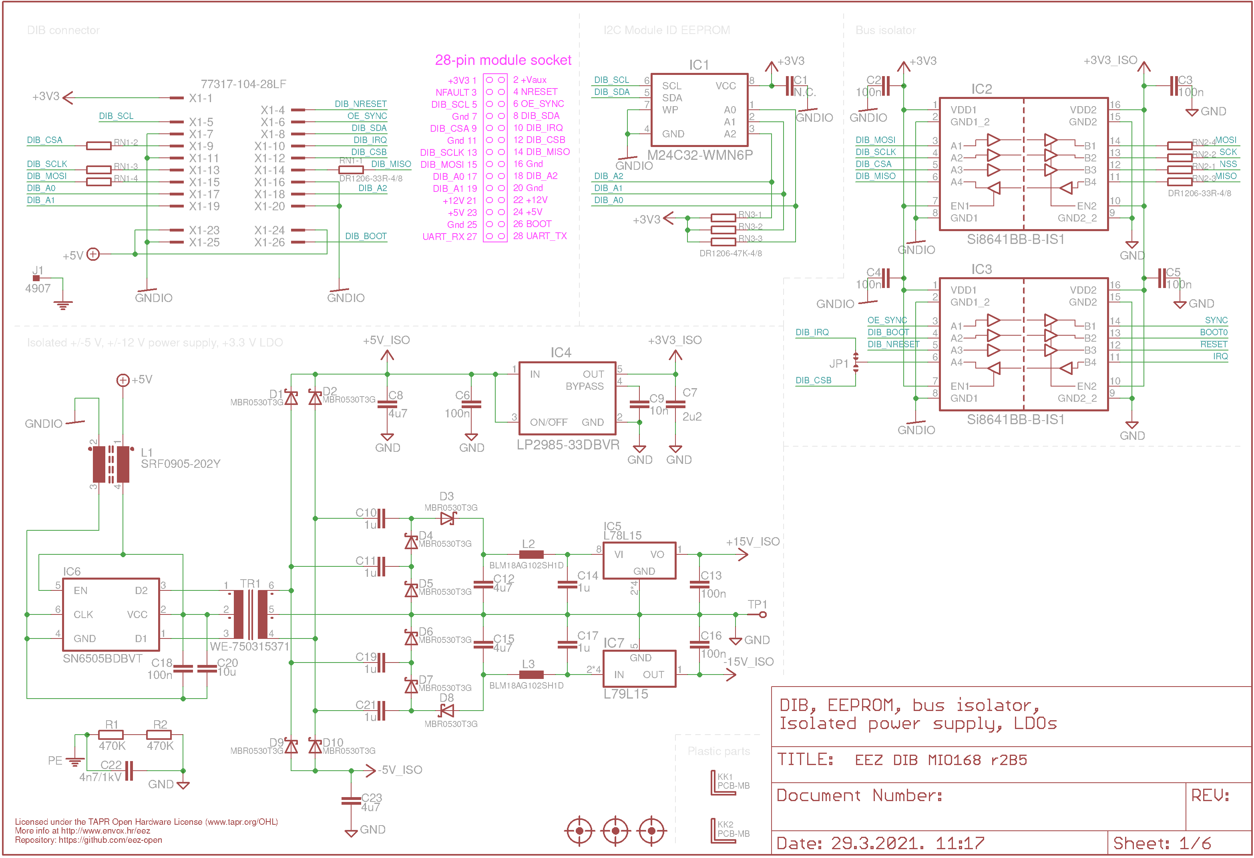
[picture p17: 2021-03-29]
EEZ DIB MIO168 r2B5 Sheet1of6.png

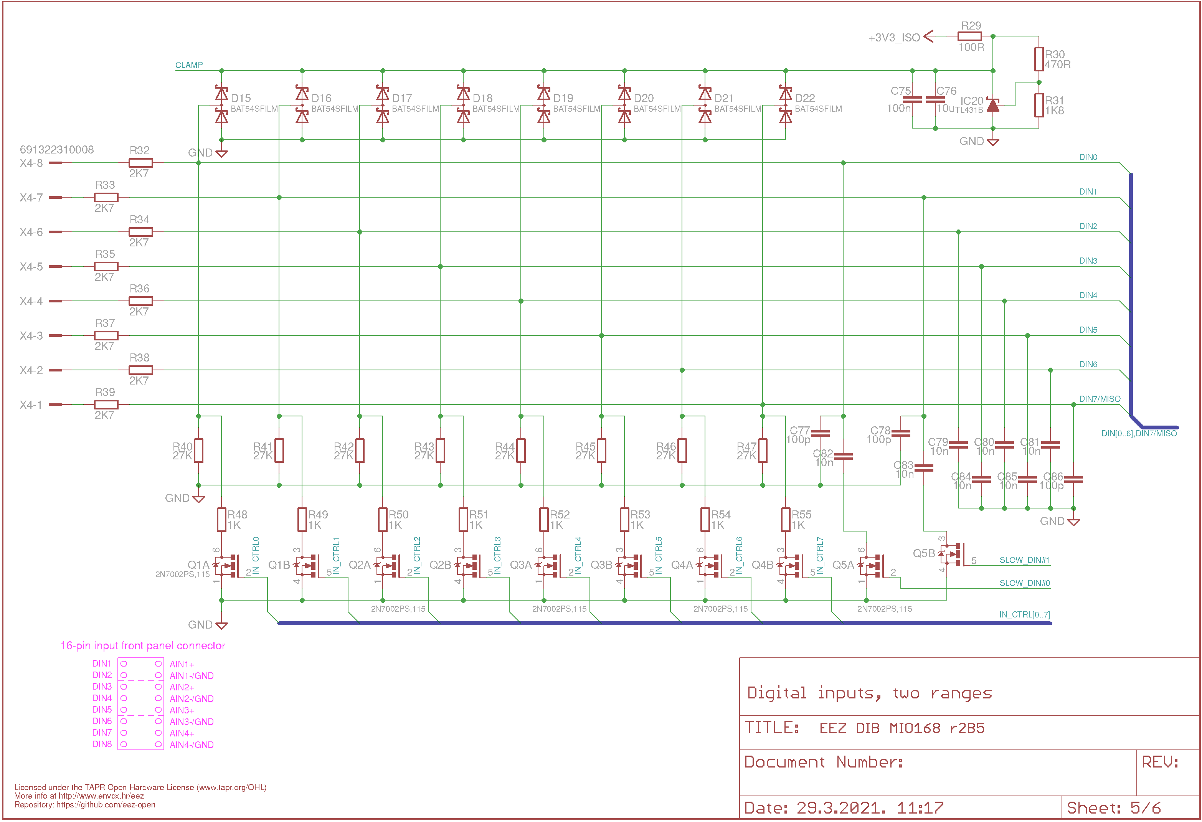
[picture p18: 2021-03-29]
EEZ DIB MIO168 r2B5 Sheet5of6.png

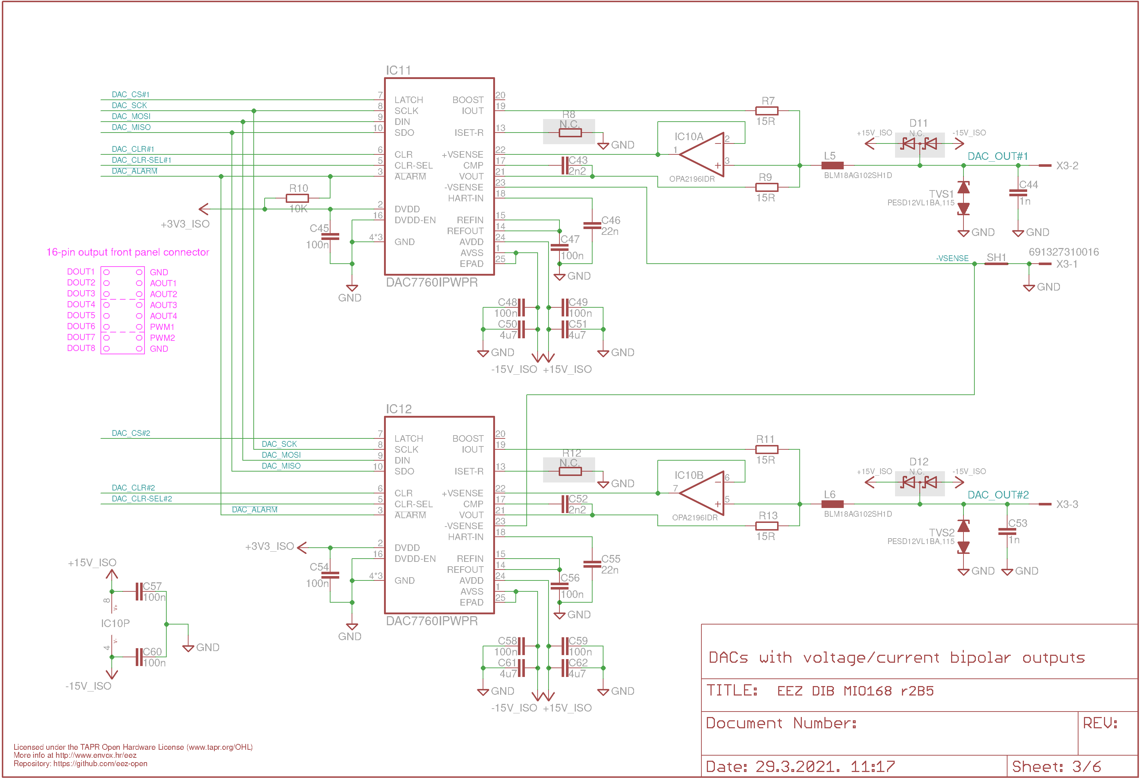
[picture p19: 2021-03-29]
EEZ DIB MIO168 r2B5 Sheet3of6.png

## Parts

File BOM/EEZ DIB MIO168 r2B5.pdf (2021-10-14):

EEZ DIB MIO168 BOM (r2B5, 2021-10-14) Project source code at https://github.com/eez-open/dib-mio168
Farnell / Element14 # Qty Part name Package Reference designator Code Part Number Unit price MOQ € | Digi-Key Part Number Unit price MOQ € | Mouser Part Number Unit price MOQ €
| | 603-CC805MKX7R7B B105
C2, C3, C4, C5, C6, C13, C0603C104K4RAC C16, C18, C28, C29, C30, 7081 C31, C32, C33, C34, C35, C36, C37, C38, C40, C45, C47, C48, C49, C54, C56, C57, C58, C59, C60, C63, C66, C67, C69, C71, C72, C73, C74, C75, C87 | | 80-C0603C104M4R
| | 810-CGA4J1X7S1C1 06KA
| | 791-1812B472K102C T
| | 710-885012006049
4u7 tant. | | 80-T491A475K006
| | 885012007065
VJ0805A102JXAC W1BC | | 710-885012007040
| | 80-C0805C223K5R
MC0805B154K160 CT | | 791-0805B154K500C T
| | 80-C0805C225M4R ECLR
C0805C101JAGAC TU | | 80-C0805C101K5G
| | 963-TMK212AB7475 MG-T
C9, C79, C80, C81, C82, VJ0805Y103JXXP C83, C84, C85 W1BC | | 710-885012207122
| 863-MBR0530T3G | MBR0530T3GOS CT-ND
D15, D16, D17, D18, D19, D20, D21, D22, D23, D24 | | 511-BAT54SFILM
| | 511-M24C32-WMN6P
| | 595-OPA2196IDR
1 | 7 1u | 0805 | 2896566 | 0.084 | 5 | 587-1283-1-ND | 0.090 | 10 | 0.062 10
2 | 40 100n | 0603 | 2522597 | 0.011 10 | 490-4774-1-ND | 0.029 100 | 0.007 100
3 | 2 10u | 1206 | C20, C76 | 3013485 | 0.262 10 | 1276-2872-1-ND | 0.207 | 10 | 0.144 | 1
4 | 1 4n7/1kV | 1812 | C22 | 2812609 | 885342211001 | 1.120 | 1 | 732-12143-1-ND | 0.660 | 10 | 0.497 | 1
5 | 2 4p7 | 0603, C0G | 2627469 | 0.329 10 | 311-1740-1-ND | 0.054 | 10 | 0.072 10
6 | 1 | 1206 | C27 | 2321209 | T491A475K006AT | 0.372 | 1 | 399-9717-1-ND | 0.270 | 10 | 0.265 10
7 | 2 2n2 | 0805, C0G | C43, C52 | 9406220 | 0.130 10 | 732-7840-1-ND | 0.097 | 10 | 0.096 10
8 | 4 1n | 0805, C0G | C44, C53, C64, C70 | 2896470 | 0.044 10 | 732-7858-1-ND | 0.055 | 10 | 0.052 10
9 | 2 22n | 0805 | C46, C55 | 9406360 | 0.065 10 | 399-1163-1-ND | 0.054 | 10 | 0.038 10
10 | 1 150n | 0805 | C65 | 1759146 | 0.073 | 5 | 1276-6476-1-ND | 0.058 | 10 | 0.066 50
11 | 3 2u2 | 0805 | C7, C41, C42 | 1828829 | 0.198 | 5 | 1276-2954-1-ND | 0.085 | 10 | 0.078 10
12 | 3 100p | 0805 | C77, C78, C86 | 2896861 | 0.023 10 | 399-15000-1-ND | 0.019 | 10 | 0.032 10
13 | 9 4u7 | 0805 | 2112841 | 0.163 | 5 | 490-14466-1-ND | 0.114 | 10 | 0.104 10
14 | 8 10n | 0805 | 2896555 | 0.065 10 | 490-7194-1-ND | 0.017 | 10 | 0.036 10
15 | 12 MBR0530T3G | SOD-123 | 2533225 | MBR0530T3G | 0.337 | 5 | 0.192 | 10 | 0.241 10
16 | 10 BAT54SFILM | SOT-23 | 9801510 | BAT54SFILM. | 0.243 25 | 497-2522-1-ND | 0.139 | 25 | 0.214 10
17 | 1 M24C32-WMN6P | SOIC-8 | IC1 | 1224413 | M24C32-WMN6P | 0.212 | 5 | - | | | 0.210 | 1
18 | 2 OPA2196IDR | SOIC-8 | IC10, IC15 | 3004863 | OPA2196ID | 2.230 | 1 | 296-48159-1-ND | 1.850 | 1 | 1.940 | 1
19 | 2 DAC7760IPWPR | HTSSOP-24 | IC11, IC12 | 3005668 | DAC7760IPWPR | 6.210 | 1 | 296-37188-1-ND | 5.400 | 1 | 5.630 | 1

C10, C11, C14, C17, C19,
C21, C39

VJ0805Y105KXXT
W1BC

CL21B106KOQNN
NE
C25, C26 | MC0603N4R7C500 CT
MCU0805C222JCT | 710-

MCU0805R223KC
T

GRM21BR71C225
KA12L

C8, C12, C15, C23, C50,
C51, C61, C62, C68

EMK212B7475KG-T

D1, D2, D3, D4, D5, D6, D7, D8, D9, D10, D25, D26

595-
DAC7760IPWPR

# Qty Part name | RS Components | TME | Price calculation for 1 set

Code Part Number Unit price MOQ € | Code / Part Number Unit price MOQ € | THT SMD

1 7 1u

2 40 100n

3 2 10u

4 1 4n7/1kV

5 2 4p7

6 1

7 2 2n2

8 4 1n

9 2 22n

10 1 150n

11 3 2u2

12 3 100p

13 9 4u7

14 8 10n

15 12 MBR0530T3G

16 10 BAT54SFILM

17 1 M24C32-WMN6P

18 2 OPA2196IDR

19 2 DAC7760IPWPR

4u7 tant.

451-5770 | 0.028 25 | CL21B105KOFNNNE | 0.010 100 | 7 | TME | 0.010 € | 7 | 0.073
393-6952 | 0.069 25 | CL10B104KA8NNNC | 0.098 100 | 40 | Mouser | 0.007 € 40 | 0.280
184-3969 | 0.233 50 | CL21A106KOQNNNG | 0.034 100 | 2 | TME | 0.034 € | 2 | 0.069
135-5684 | 0.706 20 | 1812B472K202CT | 0.237 10 | 1 | TME | 0.237 € | 1 | 0.237
298-9315 | 0.024 25 | CL10C4R7CB8NNNC | 0.024 100 | 2 | RS | 0.024 € | 2 | 0.048
538-2335 | 0.290 10 | T491A475K006AT | 0.099 10 | 1 | TME | 0.099 € | 1 | 0.099
741-4513 | 0.039 100 | 0805N222J500CT | 0.081 50 | 2 | RS | 0.039 € | 2 | 0.078
723-6408 | 0.031 100 | CL21C102JBCNNNC | 0.026 100 | 4 | TME | 0.026 € | 4 | 0.102
619-8175 | 0.036 25 | CL21B223KBANNNC | 0.018 100 | 2 | TME | 0.018 € | 2 | 0.035
198-8144 | 0.038 100 | 0.070 100 | 1 | RS | 0.038 € | 1 | 0.038
766-1031 | 0.069 100 | CL21B225KOFNNNG | 0.071 100 | 3 | RS | 0.069 € | 3 | 0.207
461-3997 | 0.030 50 | CL21C101JBANNNC | 0.026 100 | 3 | Digikey | 0.019 € | 3 | 0.057
184-3708 | 0.062 50 | 0.242 10 | 9 | RS | 0.062 € | 9 | 0.558
464-6672 | 0.026 50 | CC0805KRX7R9103 | 0.027 100 | 8 | Digikey | 0.017 € | 8 | 0.136
791-6069 MBR0530T3G | 0.076 100 | MBR0530T3G | 0.070 10 | 12 | TME | 0.070 € 12 | 0.840
189-4412 BAT54SFILMY | 0.312 50 | BAT54SFILM | 0.210 25 | 10 | Digikey | 0.139 € 10 | 1.392
686-2453 | 0.180 25 | M24C32-WMN6P | 0.165 | 3 | 1 | TME | 0.165 € | 1 | 0.165
- | | - | | | 2 | Digikey | 1.850 € | 2 | 3.700
- | | - | | | 2 | Digikey | 5.400 € | 2 | 10.800

Best
Supplier

Lowest
unit price
€

Order
Qty Line Cost €

C0805C105K4R
ACTU

VJ0603Y104KXJ
AT

EMK212BB7106
MG-T

1812GC472KAT
2A

C0603C479C5G
ACTU
T491A475K006
AT
C2012C0G1H22
2J060AA
GRM2195C1H1
02JA01D
LLL215R71E223
MA11L
CC0805KRX7R9
BB154

CC0805KRX7R9BB15
4

CL21B225KAFN
NNF

CC0805JRNP09 BN101

| C0805C475K3RACAU TO

08055C103KAT 2A

TMK212ABJ475
KG-T

M24C32-
WMN6P

# Qty Part name Package Reference designator Code Part Number Unit price MOQ € | Part Number Unit price MOQ € | Part Number Unit price MOQ €

| | 595-OPA376AIDBVR
| | 595-DAC7563TDGSR
| BTS3408GXUMA 2CT-ND | 726-BTS3408GXUMA 2
| | 634-SI8641BB-B-IS1
| | 595-TL431IDBZR
| DG212BDY-T1-E3CT-ND | 781-DG212BDY-T1-E3
| | 771-HC126PW118
| | 595-LP2985-33DBVR
| MC78L15ACDR2 GOSDKR-ND | 863-MC78L15ACDR2 G
| | 595-SN6505BDBVT
| MC79L15ABDR2 GOSDKR | 863-MC79L15ACDR2 G
| | 511-STM32F446ZCT 6

THT, PCB terminal; 4.8mm
| | 855-M22-2510305
| SRF0905-202YCT-ND | 652-SRF0905-202Y
| | 81-BLM18AG102SH 1D
20 | 1 OPA376AIDBVR | SOT-23-5 | IC13 | 3004990 | OPA376AIDBVR | 1.470 | 1 | 296-39130-1-ND | 1.460 | 1 | 1.520 | 1
21 | 1 DAC7563TDGSR | VSSOP-10 | IC14 | - | | | | 296-43287-1-ND | 5.290 | 1 | 5.240 | 1
22 | 4 BTS3408G | SOIC-8 | IC16, IC17, IC18, IC19 | 2480561 | BTS3408GXUMA2 | 1.520 | 1 | | 1.720 | 1 | 1.790 | 1
23 | 2 SI8641BB-B-IS1 | SOIC-16 | IC2, IC3 | 2423291 | SI8641BB-B-IS1 | 2.140 | 1 | 336-2566-ND | 2.230 | 1 | 2.060 | 1
24 | 1 TL431 | SOT-23 | IC20 | 3124355 | ATL431AIDBZR | 0.349 | 5 | 296-17332-1-ND | 0.270 | 1 | 0.324 | 1
25 | 1 DG212BDY-T1-E3 | SOIC-16 | IC21 | 1469429 | DG212BDY-T1-E3 | 1.820 | 1 | | 1.550 | 1 | 1.470 | 1
26 | 1 74HC126PW,118 | TSSOP-14 | IC22 | 2777722 | 74HC126PW,118 | 0.355 | 5 | 1727-6579-1-ND | 0.400 | 1 | 0.414 | 1
27 | 1 | SOT-23-5 | IC4 | 1053660 | | 0.610 | 1 | 296-18476-1-ND | 0.540 | 1 | 0.507 | 1
28 | 1 L78L15 | SOIC-8 | IC5 | 2534301 | MC78L15ACDR2G | 0.390 | 5 | | 0.340 | 1 | 0.330 | 1
29 | 1 SN6505BDBVT | SOT-23-6 | IC6 | 3008491 | SN6505BDBVT | 2.880 | 1 | 296-43154-1-ND | 2.550 | 1 | 2.480 | 1
30 | 1 L79L15 | SOIC-8 | IC7 | 2534289 | MC79L15ACDR2G | 0.370 | 5 | | 0.390 | 1 | 0.356 | 1
31 | 1 STM32F446ZCT6 | LQFP-144 | IC8 | 2488314 | STM32F446ZCT6 | 7.900 | 1 | 497-17473-ND | 6.010 | 1 | 7.120 | 1
32 | 1 4907 | J1 | - | 36-4907-ND | 0.260 | 1 | 534-4907 | 0.257 | 1
33 | 2 DS1025-01-1*3P8BV1-B | JP2, JP3 | 2289777 | M22-2510305 | 0.133 100 | 952-1312-ND | 0.189 | 10 | 0.169 10
34 | 1 SRF0905-202Y | ??? | L1 | 2112783 | SRF0905-202Y | 0.960 | 1 | | 1.140 | 1 | 0.991 | 1
35 | 6 BLM18AG102SH1D | 0603 | L2, L3, L4, L5, L6, L7 | 1515671 | 0.053 10 | 490-7809-1-ND | 0.081 | 10 | 0.063 10
36 | 5 2N7002PS,115 | SC-88 / SOT-363 | Q1, Q2, Q3, Q4, Q5 | 1859846 | 2N7002PS,115 | 0.297 | 5 | - | -
37 | 1 2N7002 | SOT-23 | Q11 | 1713823 | 2N7002-7-F | 0.118 | 5 | | 0.150 | 1 | 0.128 | 1
38 | 2 BSS84P | SOT-23 | Q6, Q8 | 1056526 | 0.224 | 5 | 0.314 | 10 | 0.196 10
39 | 1 MMBT5401 | SOT-23 | Q7 | 2533333 | MMBT5401LT3G | 0.181 | 5 | 0.154 | 10 | 0.135 10
40 | 2 MMBT5551 | SOT-23 | Q9, Q10 | 1459109 | MMBT5551LT1G | 0.154 | 5 | | 0.180 | 1 | 0.170 | 1
41 | 2 470K | 0805 | R1, R2 | 2447661 | 0.007 10 | 0.066 | 10 | 0.030 100
LP2985-33DBVR | LP2985A- 33DBVTE4 .

THT, Pin header 1x3, male, 2mm

BLM18AG102SN1
D
2N7002LT1GOS CT-ND | 863-2N7002LT1G
BSS84PH6327XTS A2 | BSS84PH6433X TMA1CT-ND | 726-BSS84PH6327X TSA2
| MMBT5401-FDICT-ND | 621-MMBT5401-F
| MMBT5551LT1G OSCT-ND | 863-MMBT5551LT1G

MCWR08X4703FT
L

13-
RT0805FRE0747
0KLDKR-ND

652-CMP0805-
FX-4703L

# Qty Part name

20 1 OPA376AIDBVR

21 1 DAC7563TDGSR

22 4 BTS3408G

23 2 SI8641BB-B-IS1

24 1 TL431

25 1 DG212BDY-T1-E3

26 1 74HC126PW,118

27 1

28 1 L78L15

29 1 SN6505BDBVT

30 1 L79L15

31 1 STM32F446ZCT6

32 1 4907
33 2 DS1025-01-1*3P8BV1-B

34 1 SRF0905-202Y

35 6 BLM18AG102SH1D

36 5 2N7002PS,115
37 1 2N7002

38 2 BSS84P

39 1 MMBT5401

40 2 MMBT5551

41 2 470K

LP2985-33DBVR

Code Part Number Unit price MOQ € | Code / Part Number Unit price MOQ € | THT SMD

Best
Supplier

Lowest
unit price
€

Order
| | | | | | | | | Qty | Line Cost €
459-550 | OPA376AIDBVT | 1.714 | 5 | - | 1 | Digikey | 1.460 € | 1 | 1.460
- | | | - | | | 1 | Mouser | 5.240 € | 1 | 5.240
825-9099 | 1.298 10 | BTS3408GXUMA2 | 1.230 | 1 | 4 | TME | 1.230 € | 4 | 4.920
823-2126 Si8641BB-B-IS1 | 2.190 | 5 | - | | | 2 | Mouser | 2.060 € | 2 | 4.120
797-4810 | 0.060 50 | L431QDBZR.215 | 0.079 10 | 1 | RS | 0.060 € | 1 | 0.060
710-4780 | 1.630 | 5 | - | | | 1 | Mouser | 1.470 € | 1 | 1.470
151-3398 | 0.291 50 | SN74HC126PW | 0.267 | 3 | 1 | TME | 0.267 € | 1 | 0.267
660-6733 LP2985-33DBVT | 0.737 | 1 | LP2985-33DBVR | 0.362 | 1 | 1 | TME | 0.362 € | 1 | 0.362
688-9272 MC78L15ACDG | 0.280 | 2 | L78L15ACD13TR | 0.083 | 5 | 1 | TME | 0.083 € | 1 | 0.083
133-0701 SN6505BDBVT | 2.520 | 1 | - | | | 1 | Mouser | 2.480 € | 1 | 2.480
785-7140 MC79L15ABDG | 0.410 | 2 | MC79L15ACDG | 0.230 | 3 | 1 | TME | 0.230 € | 1 | 0.230
189-4089 | 6.960 | 1 | - | | | 1 | Digikey | 6.010 € | 1 | 6.010
- | 61-1537-11/0031 | 0.049 10 | 1 | TME | 0.049 € | 1 | 0.049
681-3281 M22-2010305 | 0.178 10 | 0.033 10 | 2 | TME | 0.033 € | 2 | 0.067
- | | | - | | | 1 | Farnell | 0.960 € | 1 | 0.960
839-0803 | 0.043 100 | BLM18AG102SH1D | 0.016 50 | 6 | TME | 0.016 € | 6 | 0.094
781-6708 2N7002PS,115 | 0.242 50 | 2N7002PS.115 | 0.062 10 | 5 | TME | 0.062 € | 5 | 0.310
545-0012 2N7002LT1G | 0.126 50 | 2N7002LT1G | 0.025 25 | 1 | TME | 0.025 € | 1 | 0.025
- | BSS84P | 0.060 10 | 2 | TME | 0.060 € | 2 | 0.120
739-0546 MMBT5401 | 0.157 10 | MMBT5401 | 0.024 25 | 1 | TME | 0.024 € | 1 | 0.024
545-0400 | 0.146 10 | MMBT5551 | 0.024 25 | 2 | TME | 0.024 € | 2 | 0.048
223-0786 CRG0805F470K | 0.026 50 | 0805S8F4703T5E | 0.014 100 | 2 | Farnell | 0.007 € | 2 | 0.015

BTS3408GXUM
A2

TL431AMFDT,2
15
DG212BDY-T1-
E3
74HC123PW,11
8

STM32F446ZCT
6

DS1025-01-1*3P8BV1-
B

BLM18AG102S
H1D

MMBT5551LT1
G

# Qty Part name Package Reference designator Code Part Number Unit price MOQ € | Part Number Unit price MOQ € | Part Number Unit price MOQ €

R14, R16, R19, R20, R22, R26 | | 667-ERJ-PB6B9091V
| | 667-ERA-6AEB753V
MCWR08X1800FT L | | 652-CR0805FX-1800ELF
| 311-100CRCT-ND | 652-CR0805FX-1000ELF
R30, R63 | 311-470CRCT-ND | 71-CRCW0805470R FKEB
| | 652-CR0805FX-1801ELF
R32, R33, R34, R35, R36, MCWR12X2701FT R37, R38, R39 L | 311-2.70KFRCT-ND | 652-CR1206FX-2701ELF
| 311-4.70KCRCT-ND | 603-RC0805FR-074K7L
R40, R41, R42, R43, R44, MCWR08X2702FT R45, R46, R47 L | | 279-CRGCQ0805F27 K
| RC0805FR-071KL | 603-RC0805FR-071KL
RC0805FR-0710KL | 311-10.0KCRCT-ND | 603-RC0805FR-0710KL
| | 279-CRGCQ0805F47 R
MCWR08X1003FT L | RMCF0805FT10 0KCT-ND | 71-CRCW0805100K FKEAC
| RNCP0805FTD1 5R0CT-ND | 652-CR0805FX-15R0ELF
1206 resistor array | CAY16-330J4LFCT-ND | 652-CAY16-330J4LF
| | 473J4LF
Push-Pull Transformer
| | 771-PESD12VL1BA-T/R
THT, 28-pin 0.1" header right angled | | 649-77317-104-28LF
| 732-691327310016-ND
THT, 8-pin 3.81mm terminal block header, male pin | | 710-691322310008
42 | 6 9K09 0.1% | 0805 | 1810599 | ERA6AEB9091V | 0.372 10 | P9.09KDACT-ND | 0.261 | 10 | 0.145 10
43 | 4 75K 0.1% | 0805 | R15, R21, R23, R27 | 1670252 | ERA6AEB753V | 0.285 10 | P75KDACT-ND | 0.274 | 10 | 0.272 10
44 | 2 180R | 0805 | R17, R24 | 2447583 | 0.008 10 | A126343CT-ND | 0.044 | 10 | 0.032 10
45 | 3 100R | 0805 | 2447552 | 0.008 10 | 0.036 | 10 | 0.013 10
46 | 2 470R | 0805 | 1099798 | WCR0805-470RFI | 0.019 10 | 0.039 | 10 | 0.041 10
47 | 1 1K8 | 0805 | R31 | 1100316 | WCR0805-1K8FI | 0.017 10 | A129752CT-ND | 0.044 | 10 | 0.032 10
48 | 8 2K7 | 1206 | 2447497 | 0.012 10 | 0.064 | 10 | 0.027 10
49 | 1 4K7 | 0805 | R4 | 2861530 | CRGCQ0805F4K7 | 0.012 10 | 0.040 | 10 | 0.027 10
50 | 8 27K | 0805 | 2447620 | 0.008 10 | A126356CT-ND | 0.044 | 10 | 0.043 10
51 | 10 1K | 0805 | 1099800 | WCR0805-1K0FI | 0.019 10 | 0.039 | 10 | 0.015 10
52 | 5 10K | 0805 | R5, R10, R28, R62, R64 | 9237755 | 0.022 10 | 0.039 | 10 | 0.014 10
53 | 5 47R | 0805 | R6, R18, R25, R60, R66 | 2861899 | CRGCQ0805J47R | 0.007 10 | P47.0CCT-ND | 0.069 | 10 | 0.028 10
54 | 2 100K | 0805 | R61, R65 | 2447551 | 0.010 10 | 0.024 | 10 | 0.040 10
55 | 4 15R | 0805 | R7, R9, R11, R13 | 2447576 | 0.008 10 | 0.063 | 10 | 0.038 10
56 | 4 DR1206-33R-4/8 | RN1, RN2, RN5, RN6 | 1770128 | CAY16-330J4LF | 0.069 10 | 0.090 | 1 | 0.085 | 1
57 | 1 DR1206-47K-4/8 | RN3 | 2787793 | CAY16-4702F4LF | 0.178 10 | CAY16-473J4LF | 0.080 | 10 | 0.016 10
58 | 1 75031537 | TR1 | 2907256 | 75031537 | 4.550 | 1 | 1297-1178-1-ND | 2.060 | 1 | 710-750315371 | 2.120 | 1
59 | 4 PESD12VL1BA,115 | SOD-323 | TVS1, TVS2, TVS3, TVS4 | 8737363 | 0.365 | 5 | 1727-3808-1-ND | 0.320 | 10 | 0.296 10
60 | 1 77317-104-28LF | X1 | - | | | | S2111EC-14-ND | 1.030 | 1 | | 1.540 | 1
61 | 1 691327310016 | X3 | 1793077 | | 5.770 | 1 | | 7.810 | 1 | 651-1843130 | 9.270 | 1
62 | 1 691322310008 | X4 | 1705378 | EB3-08-B | 2.250 | 1 | 732-2093-ND | 1.360 | 1 | | 1.400 | 1
63 | 2 DS1014-10RF1B | X5, X6 | - | | | | - | | | -
R29, R58, R59 | MCWR08X1000FT L

R48, R49, R50, R51, R52,
R53, R54, R55, R56, R57

MCWR08X15R0FT
L
1206 resistor array | 652-CAY16-

PESD12VL1BA,11
5

THT, 16-pin 3.81mm terminal block header, male pins

MCD 1,5/ 8-G1-
3,81

THT, 10-pin IDC Socket 2mm, angled 90°

# Qty Part name

42 6 9K09 0.1%

43 4 75K 0.1%

44 2 180R

45 3 100R

46 2 470R

47 1 1K8

48 8 2K7

49 1 4K7

50 8 27K

51 10 1K

52 5 10K

53 5 47R

54 2 100K

55 4 15R

56 4 DR1206-33R-4/8

57 1 DR1206-47K-4/8

58 1 75031537
59 4 PESD12VL1BA,115

60 1 77317-104-28LF

61 1 691327310016

62 1 691322310008

63 2 DS1014-10RF1B

Code Part Number Unit price MOQ € | Code / Part Number Unit price MOQ € | THT SMD

Best
Supplier

Lowest
unit price
€

Order
Qty | Line Cost €
904-8648 ERA6ARB9091V | 0.142 100 | ERA6AEB9091V | 0.081 10 | 6 | TME | 0.081 € | 6 | 0.486
828-0673 ERA6AEB753V | 0.470 | 5 | ERA6AEB753V | 0.081 10 | 4 | TME | 0.081 € | 4 | 0.324
223-0326 CRG0805F180R | 0.030 50 | 0805S8F1800T5E | 0.016 100 | 2 | Farnell | 0.008 € | 2 | 0.016
125-1188 CRG0805F100R | 0.004 100 | 0805S8F1000T5E | 0.015 100 | 3 | RS | 0.004 € | 3 | 0.012
223-0376 CRG0805F470R | 0.021 50 | RC0805FR-07470R | 0.022 100 | 2 | Farnell | 0.019 € | 2 | 0.038
679-1033 | 0.004 50 | 0805S8J0182T5E | 0.014 100 | 1 | RS | 0.004 € | 1 | 0.004
223-2322 CRG1206F2K7 | 0.030 50 | 1206S4F2701T5E | 0.019 100 | 8 | Farnell | 0.012 € | 8 | 0.097
223-0528 CRG0805F4K7 | 0.023 50 | 0805S8F4701T5E | 0.023 100 | 1 | Farnell | 0.012 € | 1 | 0.012
223-0613 CRG0805F27K | 0.026 50 | 0805S8F2702T5E | 0.016 100 | 8 | Farnell | 0.008 € | 8 | 0.062
223-0427 CRG0805F1K0 | 0.017 50 | RC0805FR-071K | 0.022 100 | 10 | Mouser | 0.015 € 10 | 0.150
125-1189 CRG0805F10K | 0.002 100 | RC0805FR-0710K | 0.022 100 | 5 | RS | 0.002 € | 5 | 0.010
223-0253 CRG0805F47R | 0.016 50 | SMD0805-47R-1% | 0.022 100 | 5 | Farnell | 0.007 € | 5 | 0.033
223-0691 CRG0805F100K | 0.028 50 | 0805S8F1003T5E | 0.015 100 | 2 | Farnell | 0.010 € | 2 | 0.019
679-0914 | 0.004 50 | 0805S8F150JT5E | 0.016 100 | 4 | RS | 0.004 € | 4 | 0.016
522-5670 CAY16-330J4LF | 0.004 50 | 4D03WGJ0330T | 0.009 100 | 4 | RS | 0.004 € | 4 | 0.016
522-5759 CAY16-473J4LF | 0.020 50 | 4D03WGJ0473T | 0.013 100 | 1 | TME | 0.013 € | 1 | 0.013
182-8977 750315371 | 2.560 | 1 | - | 1 | Digikey | 2.060 € | 1 | 2.060
508-024 | 0.294 20 | PESD12VL1BA.115 | 0.126 | 5 | 4 | TME | 0.126 € | 4 | 0.504
- | - | 1 | Digikey | 1.030 € | 1 | 1.030
191-1724 691327310016 | 7.900 | 1 | - | 1 | Farnell | 5.770 € | 1 | 5.770
824-6661 691322310008 | 1.470 | 1 | 0.651 | 1 | 1 | TME | 0.651 € | 1 | 0.651
- | DS1014-10RF1B | 0.220 | 3 | 2 | TME | 0.220 € | 2 | 0.440

CRCW08051K8
0FKEA

CRCW080515R
0FKEA

PESD12VL1BA,
115

15EDGRC-3.81-08P-14-00A(H)

# Qty Part name Package Reference designator Code Part Number Unit price MOQ € | Part Number Unit price MOQ € | Part Number Unit price MOQ €

THT, 28-pin 2.54 mm 2x14 receptacle | | 200-SSQ11401TD
| | 449-LFXTAL026392B ULK
| SMAJ16A-FDICT-ND | 621-SMAJ16A-13-F
64 | 2 DS1023-2*14S21 | X7, X8 | 3570684 | SSQ-114-01-T-D | 2.680 | 1 | SAM1183-14-ND | 2.070 | 1 | 2.130 | 1
65 | 1 LF XTAL026392 | Y1 | 1276696 | LFXTAL026392 | 1.250 | 1 | 1923-1009-ND | 0.850 | 1 | 0.972 | 1
66 | 2 SMAJ16 | SMA | ZD1, ZD2 | 3577011 | SMAJ16A-13-F | 0.104 | 5 | 0.400 | 1 | 0.356 | 1
1 N.C. | 0603 | C1
2 N.C. | 0805 | C88, C89
1 N.C. | 0805 | C24
4 N.C. | | D11, D12, D13, D14
1 N.C. | | IC9
1 503398-1892 Micro SD, push-push, 8-pin J2 2358234 503398-1892 1.980 1 | WM11190CT-ND 2.160 1 | 538-503398-1.960 1
| | 1892
1 N.C. 0805 RN4
3 N.C. | 0805 | R3, R8, R12
1 N.C. | | X2
2 PMB-1 | KK1, KK2 | - | - | -
2 JUMPER-2.0/R
4 TJ0831530000G | 2579776 | EBK-08-B | 2.400 | 1 | 609-3803-ND | 1.760 | 1 | 1.530 | 1
1 | -

16 MHz XTAL;
7.5x5.1x1.4mm

Not installed

Related parts and accessories PCB bracket; polyamide
2mm jumper
8-pin 3.81mm pluggable
terminal block

649-220004-
D081B01LF

Custom made components
PCB 4-layer 146 x 95
mm

All prices are net prices (without VAT)

Please note that BOM does not contain ordering number for parts on reels or that which includes re-reeling fee (e.g. Farnell). Take also into account that total cost is higher because min. quantity (MOQ) for many parts is larger then what is needed for single unit.

All resistors are 1% 0805 and all capacitors are X7R 0805 if not otherwise specified.

# Qty Part name

64 2 DS1023-2*14S21

65 1 LF XTAL026392

66 2 SMAJ16

1 N.C.
2 N.C.
1 N.C.
4 N.C.
1 N.C.
1 503398-1892
3 N.C.
1 N.C.
1 N.C.

2 PMB-1
2 JUMPER-2.0/R
4 TJ0831530000G

1

Not installed

Related parts and accessories

Custom made components
PCB 4-layer 146 x 95
mm
Code Part Number Unit price MOQ € | Code / Part Number Unit price MOQ € | THT SMD
| SSQ-114-01-T-D

Best
Supplier

Lowest
unit price
€

Order
| | | | | | | | | Qty | Line Cost €
207-9041 | 2.820 | 1 | DS1023-2*14S21 | 0.326 | 2 | 2 | TME | 0.326 € | 2 | 0.651
148-4357 LFXTAL026392 | 0.960 10 | 16.00M-12SM | 0.950 | 1 | 1 | Digikey | 0.850 € | 1 | 0.850
171-9586 SMAJ16A | 0.149 25 | SMAJ16A-13-F | 5 | 2 | Farnell | 0.104 € | 2 | 0.208
10 | 222 | 60.80 €
| | | | | | 1 | Farnell | 0.000 € | 1 | 0.000
| | | | | | 1 | Farnell | 0.000 € | 1 | 0.000
| | | | | | 4 | Farnell | 0.000 € | 4 | 0.000
| | | | | | 1 | Farnell | 0.000 € | 1 | 0.000
880-1277 503398-1892 | 2.600 | 1 | MX-503398-1892 | 0.860 | 2 | 1 | TME | 0.860 € | 1 | 0.860
| | | | | | 3 | Farnell | 0.000 € | 3 | 0.000
| | | | | | 1 | Farnell | 0.000 € | 1 | 0.000
| | | | | | 1 | Farnell | 0.000 € | 1 | 0.000
- | PMB-1 | 0.072 10 | TME | 0.072 € | 2 | 0.145
JUMPER-2.0/R | 0.045 20 | TME | 0.045 € | 2 | 0.089
- | 1.430 | 1 | TME | 1.430 € | 4 | 5.720

5.95 €

JLCPCB | 11.374 € | 1 | 11.374
| | | 11.37 €

78.12 €

15EDGK-3.81-08P-14-
00A(H)

Total

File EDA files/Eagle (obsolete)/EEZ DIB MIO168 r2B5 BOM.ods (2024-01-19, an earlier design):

 |  |  |  |  | Farnell / Element14 |  |  |  | Digi-Key |  |  | Mouser |  |  | RS Components |  |  |  | TME |  |  |  |  | Price calculation for 1 set
# | Qty | Part name | Package | Reference designator | Code | Part Number | Unit price € | MOQ | Part Number | Unit price € | MOQ | Part Number | Unit price € | MOQ | Code | Part Number | Unit price € | MOQ | Code / Part Number | Unit price € | MOQ | THT | SMD | Best Supplier | Lowest unit price € | Order Qty | Line Cost €
1 | 7 | 1u | 0805 | C10, C11, C14, C17, C19, C21, C39 | 2896566 | VJ0805Y105KXXTW1BC | 0,084 | 5 | 587-1283-1-ND | 0,090 | 10 | 603-CC805MKX7R7BB105 | 0,062 | 10 | 451-5770 | C0805C105K4RACTU | 0,028 | 25 | CL21B105KOFNNNE | 0,010 | 100 |  | 7 | TME | 0,010 € | 7 | 0,073
2 | 40 | 100n | 0603 | C2, C3, C4, C5, C6, C13, C16, C18, C28, C29, C30, C31, C32, C33, C34, C35, C36, C37, C38, C40, C45, C47, C48, C49, C54, C56, C57, C58, C59, C60, C63, C66, C67, C69, C71, C72, C73, C74, C75, C87 | 2522597 | C0603C104K4RAC7081 | 0,011 | 10 | 490-4774-1-ND | 0,029 | 100 | 80-C0603C104M4R | 0,007 | 100 | 393-6952 | VJ0603Y104KXJAT | 0,069 | 25 | CL10B104KA8NNNC | 0,098 | 100 |  | 40 | Mouser | 0,007 € | 40 | 0,280
3 | 2 | 10u | 1206 | C20, C76 | 3013485 | CL21B106KOQNNNE | 0,262 | 10 | 1276-2872-1-ND | 0,207 | 10 | 810-CGA4J1X7S1C106KA | 0,144 | 1 | 184-3969 | EMK212BB7106MG-T | 0,233 | 50 | CL21A106KOQNNNG | 0,034 | 100 |  | 2 | TME | 0,034 € | 2 | 0,069
4 | 1 | 4n7/1kV | 1812 | C22 | 2812609 | 885342211001 | 1,120 | 1 | 732-12143-1-ND | 0,660 | 10 | 791-1812B472K102CT | 0,497 | 1 | 135-5684 | 1812GC472KAT2A | 0,706 | 20 | 1812B472K202CT | 0,237 | 10 |  | 1 | TME | 0,237 € | 1 | 0,237
5 | 2 | 4p7 | 0603, C0G | C25, C26 | 2627469 | MC0603N4R7C500CT | 0,329 | 10 | 311-1740-1-ND | 0,054 | 10 | 710-885012006049 | 0,072 | 10 | 298-9315 | C0603C479C5GACTU | 0,024 | 25 | CL10C4R7CB8NNNC | 0,024 | 100 |  | 2 | RS | 0,024 € | 2 | 0,048
6 | 1 | 4u7 tant. | 1206 | C27 | 2321209 | T491A475K006AT | 0,372 | 1 | 399-9717-1-ND | 0,270 | 10 | 80-T491A475K006 | 0,265 | 10 | 538-2335 | T491A475K006AT | 0,290 | 10 | T491A475K006AT | 0,099 | 10 |  | 1 | TME | 0,099 € | 1 | 0,099
7 | 2 | 2n2 | 0805, C0G | C43, C52 | 9406220 | MCU0805C222JCT | 0,130 | 10 | 732-7840-1-ND | 0,097 | 10 | 710-885012007065 | 0,096 | 10 | 741-4513 | C2012C0G1H222J060AA | 0,039 | 100 | 0805N222J500CT | 0,081 | 50 |  | 2 | RS | 0,039 € | 2 | 0,078
8 | 4 | 1n | 0805, C0G | C44, C53, C64, C70 | 2896470 | VJ0805A102JXACW1BC | 0,044 | 10 | 732-7858-1-ND | 0,055 | 10 | 710-885012007040 | 0,052 | 10 | 723-6408 | GRM2195C1H102JA01D | 0,031 | 100 | CL21C102JBCNNNC | 0,026 | 100 |  | 4 | TME | 0,026 € | 4 | 0,102
9 | 2 | 22n | 0805 | C46, C55 | 9406360 | MCU0805R223KCT | 0,065 | 10 | 399-1163-1-ND | 0,054 | 10 | 80-C0805C223K5R | 0,038 | 10 | 619-8175 | LLL215R71E223MA11L | 0,036 | 25 | CL21B223KBANNNC | 0,018 | 100 |  | 2 | TME | 0,018 € | 2 | 0,035
10 | 1 | 150n | 0805 | C65 | 1759146 | MC0805B154K160CT | 0,073 | 5 | 1276-6476-1-ND | 0,058 | 10 | 791-0805B154K500CT | 0,066 | 50 | 198-8144 | CC0805KRX7R9BB154 | 0,038 | 100 | CC0805KRX7R9BB154 | 0,070 | 100 |  | 1 | RS | 0,038 € | 1 | 0,038
11 | 3 | 2u2 | 0805 | C7, C41, C42 | 1828829 | GRM21BR71C225KA12L | 0,198 | 5 | 1276-2954-1-ND | 0,085 | 10 | 80-C0805C225M4RECLR | 0,078 | 10 | 766-1031 | CL21B225KAFNNNF | 0,069 | 100 | CL21B225KOFNNNG | 0,071 | 100 |  | 3 | RS | 0,069 € | 3 | 0,207
12 | 3 | 100p | 0805 | C77, C78, C86 | 2896861 | C0805C101JAGACTU | 0,023 | 10 | 399-15000-1-ND | 0,019 | 10 | 80-C0805C101K5G | 0,032 | 10 | 461-3997 | CC0805JRNP09BN101 | 0,030 | 50 | CL21C101JBANNNC | 0,026 | 100 |  | 3 | Digikey | 0,019 € | 3 | 0,057
13 | 9 | 4u7 | 0805 | C8, C12, C15, C23, C50, C51, C61, C62, C68 | 2112841 | EMK212B7475KG-T | 0,163 | 5 | 490-14466-1-ND | 0,114 | 10 | 963-TMK212AB7475MG-T | 0,104 | 10 | 184-3708 | TMK212ABJ475KG-T | 0,062 | 50 | C0805C475K3RACAUTO | 0,242 | 10 |  | 9 | RS | 0,062 € | 9 | 0,558
14 | 8 | 10n | 0805 | C9, C79, C80, C81, C82, C83, C84, C85 | 2896555 | VJ0805Y103JXXPW1BC | 0,065 | 10 | 490-7194-1-ND | 0,017 | 10 | 710-885012207122 | 0,036 | 10 | 464-6672 | 08055C103KAT2A | 0,026 | 50 | CC0805KRX7R9103 | 0,027 | 100 |  | 8 | Digikey | 0,017 € | 8 | 0,136
15 | 12 | MBR0530T3G | SOD-123 | D1, D2, D3, D4, D5, D6, D7, D8, D9, D10, D25, D26 | 2533225 | MBR0530T3G | 0,337 | 5 | 863-MBR0530T3G | 0,192 | 10 | MBR0530T3GOSCT-ND | 0,241 | 10 | 791-6069 | MBR0530T3G | 0,076 | 100 | MBR0530T3G | 0,070 | 10 |  | 12 | TME | 0,070 € | 12 | 0,840
16 | 10 | BAT54SFILM | SOT-23 | D15, D16, D17, D18, D19, D20, D21, D22, D23, D24 | 9801510 | BAT54SFILM. | 0,243 | 25 | 497-2522-1-ND | 0,139 | 25 | 511-BAT54SFILM | 0,214 | 10 | 189-4412 | BAT54SFILMY | 0,312 | 50 | BAT54SFILM | 0,210 | 25 |  | 10 | Digikey | 0,139 € | 10 | 1,392
17 | 1 | M24C32-WMN6P | SOIC-8 | IC1 | 1224413 | M24C32-WMN6P | 0,212 | 5 | - |  |  | 511-M24C32-WMN6P | 0,210 | 1 | 686-2453 | M24C32-WMN6P | 0,180 | 25 | M24C32-WMN6P | 0,165 | 3 |  | 1 | TME | 0,165 € | 1 | 0,165
18 | 2 | OPA2196IDR | SOIC-8 | IC10, IC15 | 3004863 | OPA2196ID | 2,230 | 1 | 296-48159-1-ND | 1,850 | 1 | 595-OPA2196IDR | 1,940 | 1 | - |  |  |  | - |  |  |  | 2 | Digikey | 1,850 € | 2 | 3,700
19 | 2 | DAC7760IPWPR | HTSSOP-24 | IC11, IC12 | 3005668 | DAC7760IPWPR | 6,210 | 1 | 296-37188-1-ND | 5,400 | 1 | 595-DAC7760IPWPR | 5,630 | 1 | - |  |  |  | - |  |  |  | 2 | Digikey | 5,400 € | 2 | 10,800
20 | 1 | OPA376AIDBVR | SOT-23-5 | IC13 | 3004990 | OPA376AIDBVR | 1,470 | 1 | 296-39130-1-ND | 1,460 | 1 | 595-OPA376AIDBVR | 1,520 | 1 | 459-550 | OPA376AIDBVT | 1,714 | 5 | - |  |  |  | 1 | Digikey | 1,460 € | 1 | 1,460
21 | 1 | DAC7563TDGSR | VSSOP-10 | IC14 | - |  |  |  | 296-43287-1-ND | 5,290 | 1 | 595-DAC7563TDGSR | 5,240 | 1 | - |  |  |  | - |  |  |  | 1 | Mouser | 5,240 € | 1 | 5,240
22 | 4 | BTS3408G | SOIC-8 | IC16, IC17, IC18, IC19 | 2480561 | BTS3408GXUMA2 | 1,520 | 1 | BTS3408GXUMA2CT-ND | 1,720 | 1 | 726-BTS3408GXUMA2 | 1,790 | 1 | 825-9099 | BTS3408GXUMA2 | 1,298 | 10 | BTS3408GXUMA2 | 1,230 | 1 |  | 4 | TME | 1,230 € | 4 | 4,920
23 | 2 | SI8641BB-B-IS1 | SOIC-16 | IC2, IC3 | 2423291 | SI8641BB-B-IS1 | 2,140 | 1 | 336-2566-ND | 2,230 | 1 | 634-SI8641BB-B-IS1 | 2,060 | 1 | 823-2126 | Si8641BB-B-IS1 | 2,190 | 5 | - |  |  |  | 2 | Mouser | 2,060 € | 2 | 4,120
24 | 1 | TL431 | SOT-23 | IC20 | 3124355 | ATL431AIDBZR | 0,349 | 5 | 296-17332-1-ND | 0,270 | 1 | 595-TL431IDBZR | 0,324 | 1 | 797-4810 | TL431AMFDT,215 | 0,060 | 50 | L431QDBZR.215 | 0,079 | 10 |  | 1 | RS | 0,060 € | 1 | 0,060
25 | 1 | DG212BDY-T1-E3 | SOIC-16 | IC21 | 1469429 | DG212BDY-T1-E3 | 1,820 | 1 | DG212BDY-T1-E3CT-ND | 1,550 | 1 | 781-DG212BDY-T1-E3 | 1,470 | 1 | 710-4780 | DG212BDY-T1-E3 | 1,630 | 5 | - |  |  |  | 1 | Mouser | 1,470 € | 1 | 1,470
26 | 1 | 74HC126PW,118 | TSSOP-14 | IC22 | 2777722 | 74HC126PW,118 | 0,355 | 5 | 1727-6579-1-ND | 0,400 | 1 | 771-HC126PW118 | 0,414 | 1 | 151-3398 | 74HC123PW,118 | 0,291 | 50 | SN74HC126PW | 0,267 | 3 |  | 1 | TME | 0,267 € | 1 | 0,267
27 | 1 | LP2985-33DBVR | SOT-23-5 | IC4 | 1053660 | LP2985A-33DBVTE4 . | 0,610 | 1 | 296-18476-1-ND | 0,540 | 1 | 595-LP2985-33DBVR | 0,507 | 1 | 660-6733 | LP2985-33DBVT | 0,737 | 1 | LP2985-33DBVR | 0,362 | 1 |  | 1 | TME | 0,362 € | 1 | 0,362
28 | 1 | L78L15 | SOIC-8 | IC5 | 2534301 | MC78L15ACDR2G | 0,390 | 5 | MC78L15ACDR2GOSDKR-ND | 0,340 | 1 | 863-MC78L15ACDR2G | 0,330 | 1 | 688-9272 | MC78L15ACDG | 0,280 | 2 | L78L15ACD13TR | 0,083 | 5 |  | 1 | TME | 0,083 € | 1 | 0,083
29 | 1 | SN6505BDBVT | SOT-23-6 | IC6 | 3008491 | SN6505BDBVT | 2,880 | 1 | 296-43154-1-ND | 2,550 | 1 | 595-SN6505BDBVT | 2,480 | 1 | 133-0701 | SN6505BDBVT | 2,520 | 1 | - |  |  |  | 1 | Mouser | 2,480 € | 1 | 2,480
30 | 1 | L79L15 | SOIC-8 | IC7 | 2534289 | MC79L15ACDR2G | 0,370 | 5 | MC79L15ABDR2GOSDKR | 0,390 | 1 | 863-MC79L15ACDR2G | 0,356 | 1 | 785-7140 | MC79L15ABDG | 0,410 | 2 | MC79L15ACDG | 0,230 | 3 |  | 1 | TME | 0,230 € | 1 | 0,230
31 | 1 | STM32F446ZCT6 | LQFP-144 | IC8 | 2488314 | STM32F446ZCT6 | 7,900 | 1 | 497-17473-ND | 6,010 | 1 | 511-STM32F446ZCT6 | 7,120 | 1 | 189-4089 | STM32F446ZCT6 | 6,960 | 1 | - |  |  |  | 1 | Digikey | 6,010 € | 1 | 6,010
32 | 1 | 4907 | THT, PCB terminal; 4.8mm | J1 | - |  |  |  | 36-4907-ND | 0,260 | 1 | 534-4907 | 0,257 | 1 | - |  |  |  | 61-1537-11/0031 | 0,049 | 10 | 1 |  | TME | 0,049 € | 1 | 0,049
33 | 2 | DS1025-01-1*3P8BV1-B | THT, Pin header 1x3, male, 2mm | JP2, JP3 | 2289777 | M22-2510305 | 0,133 | 100 | 952-1312-ND | 0,189 | 10 | 855-M22-2510305 | 0,169 | 10 | 681-3281 | M22-2010305 | 0,178 | 10 | DS1025-01-1*3P8BV1-B | 0,033 | 10 | 2 |  | TME | 0,033 € | 2 | 0,067
34 | 1 | SRF0905-202Y | ??? | L1 | 2112783 | SRF0905-202Y | 0,960 | 1 | SRF0905-202YCT-ND | 1,140 | 1 | 652-SRF0905-202Y | 0,991 | 1 | - |  |  |  | - |  |  |  | 1 | Farnell | 0,960 € | 1 | 0,960
35 | 6 | BLM18AG102SH1D | 0603 | L2, L3, L4, L5, L6, L7 | 1515671 | BLM18AG102SN1D | 0,053 | 10 | 490-7809-1-ND | 0,081 | 10 | 81-BLM18AG102SH1D | 0,063 | 10 | 839-0803 | BLM18AG102SH1D | 0,043 | 100 | BLM18AG102SH1D | 0,016 | 50 |  | 6 | TME | 0,016 € | 6 | 0,094
36 | 5 | 2N7002PS,115 | SC-88 / SOT-363 | Q1, Q2, Q3, Q4, Q5 | 1859846 | 2N7002PS,115 | 0,297 | 5 | - |  |  | - |  |  | 781-6708 | 2N7002PS,115 | 0,242 | 50 | 2N7002PS.115 | 0,062 | 10 |  | 5 | TME | 0,062 € | 5 | 0,310
37 | 1 | 2N7002 | SOT-23 | Q11 | 1713823 | 2N7002-7-F | 0,118 | 5 | 2N7002LT1GOSCT-ND | 0,150 | 1 | 863-2N7002LT1G | 0,128 | 1 | 545-0012 | 2N7002LT1G | 0,126 | 50 | 2N7002LT1G | 0,025 | 25 |  | 1 | TME | 0,025 € | 1 | 0,025
38 | 2 | BSS84P | SOT-23 | Q6, Q8 | 1056526 | BSS84PH6327XTSA2 | 0,224 | 5 | BSS84PH6433XTMA1CT-ND | 0,314 | 10 | 726-BSS84PH6327XTSA2 | 0,196 | 10 | - |  |  |  | BSS84P | 0,060 | 10 |  | 2 | TME | 0,060 € | 2 | 0,120
39 | 1 | MMBT5401 | SOT-23 | Q7 | 2533333 | MMBT5401LT3G | 0,181 | 5 | MMBT5401-FDICT-ND | 0,154 | 10 | 621-MMBT5401-F | 0,135 | 10 | 739-0546 | MMBT5401 | 0,157 | 10 | MMBT5401 | 0,024 | 25 |  | 1 | TME | 0,024 € | 1 | 0,024
40 | 2 | MMBT5551 | SOT-23 | Q9, Q10 | 1459109 | MMBT5551LT1G | 0,154 | 5 | MMBT5551LT1GOSCT-ND | 0,180 | 1 | 863-MMBT5551LT1G | 0,170 | 1 | 545-0400 | MMBT5551LT1G | 0,146 | 10 | MMBT5551 | 0,024 | 25 |  | 2 | TME | 0,024 € | 2 | 0,048
41 | 2 | 470K | 0805 | R1, R2 | 2447661 | MCWR08X4703FTL | 0,007 | 10 | 13-RT0805FRE07470KLDKR-ND | 0,066 | 10 | 652-CMP0805-FX-4703L | 0,030 | 100 | 223-0786 | CRG0805F470K | 0,026 | 50 | 0805S8F4703T5E | 0,014 | 100 |  | 2 | Farnell | 0,007 € | 2 | 0,015
42 | 6 | 9K09 0.1% | 0805 | R14, R16, R19, R20, R22, R26 | 1810599 | ERA6AEB9091V | 0,372 | 10 | P9.09KDACT-ND | 0,261 | 10 | 667-ERJ-PB6B9091V | 0,145 | 10 | 904-8648 | ERA6ARB9091V | 0,142 | 100 | ERA6AEB9091V | 0,081 | 10 |  | 6 | TME | 0,081 € | 6 | 0,486
43 | 4 | 75K 0.1% | 0805 | R15, R21, R23, R27 | 1670252 | ERA6AEB753V | 0,285 | 10 | P75KDACT-ND | 0,274 | 10 | 667-ERA-6AEB753V | 0,272 | 10 | 828-0673 | ERA6AEB753V | 0,470 | 5 | ERA6AEB753V | 0,081 | 10 |  | 4 | TME | 0,081 € | 4 | 0,324
44 | 2 | 180R | 0805 | R17, R24 | 2447583 | MCWR08X1800FTL | 0,008 | 10 | A126343CT-ND | 0,044 | 10 | 652-CR0805FX-1800ELF | 0,032 | 10 | 223-0326 | CRG0805F180R | 0,030 | 50 | 0805S8F1800T5E | 0,016 | 100 |  | 2 | Farnell | 0,008 € | 2 | 0,016
45 | 3 | 100R | 0805 | R29, R58, R59 | 2447552 | MCWR08X1000FTL | 0,008 | 10 | 311-100CRCT-ND | 0,036 | 10 | 652-CR0805FX-1000ELF | 0,013 | 10 | 125-1188 | CRG0805F100R | 0,004 | 100 | 0805S8F1000T5E | 0,015 | 100 |  | 3 | RS | 0,004 € | 3 | 0,012
46 | 2 | 470R | 0805 | R30, R63 | 1099798 | WCR0805-470RFI | 0,019 | 10 | 311-470CRCT-ND | 0,039 | 10 | 71-CRCW0805470RFKEB | 0,041 | 10 | 223-0376 | CRG0805F470R | 0,021 | 50 | RC0805FR-07470R | 0,022 | 100 |  | 2 | Farnell | 0,019 € | 2 | 0,038
47 | 1 | 1K8 | 0805 | R31 | 1100316 | WCR0805-1K8FI | 0,017 | 10 | A129752CT-ND | 0,044 | 10 | 652-CR0805FX-1801ELF | 0,032 | 10 | 679-1033 | CRCW08051K80FKEA | 0,004 | 50 | 0805S8J0182T5E | 0,014 | 100 |  | 1 | RS | 0,004 € | 1 | 0,004
48 | 8 | 2K7 | 1206 | R32, R33, R34, R35, R36, R37, R38, R39 | 2447497 | MCWR12X2701FTL | 0,012 | 10 | 311-2.70KFRCT-ND | 0,064 | 10 | 652-CR1206FX-2701ELF | 0,027 | 10 | 223-2322 | CRG1206F2K7 | 0,030 | 50 | 1206S4F2701T5E | 0,019 | 100 |  | 8 | Farnell | 0,012 € | 8 | 0,097
49 | 1 | 4K7 | 0805 | R4 | 2861530 | CRGCQ0805F4K7 | 0,012 | 10 | 311-4.70KCRCT-ND | 0,040 | 10 | 603-RC0805FR-074K7L | 0,027 | 10 | 223-0528 | CRG0805F4K7 | 0,023 | 50 | 0805S8F4701T5E | 0,023 | 100 |  | 1 | Farnell | 0,012 € | 1 | 0,012
50 | 8 | 27K | 0805 | R40, R41, R42, R43, R44, R45, R46, R47 | 2447620 | MCWR08X2702FTL | 0,008 | 10 | A126356CT-ND | 0,044 | 10 | 279-CRGCQ0805F27K | 0,043 | 10 | 223-0613 | CRG0805F27K | 0,026 | 50 | 0805S8F2702T5E | 0,016 | 100 |  | 8 | Farnell | 0,008 € | 8 | 0,062
51 | 10 | 1K | 0805 | R48, R49, R50, R51, R52, R53, R54, R55, R56, R57 | 1099800 | WCR0805-1K0FI | 0,019 | 10 | RC0805FR-071KL | 0,039 | 10 | 603-RC0805FR-071KL | 0,015 | 10 | 223-0427 | CRG0805F1K0 | 0,017 | 50 | RC0805FR-071K | 0,022 | 100 |  | 10 | Mouser | 0,015 € | 10 | 0,150
52 | 5 | 10K | 0805 | R5, R10, R28, R62, R64 | 9237755 | RC0805FR-0710KL | 0,022 | 10 | 311-10.0KCRCT-ND | 0,039 | 10 | 603-RC0805FR-0710KL | 0,014 | 10 | 125-1189 | CRG0805F10K | 0,002 | 100 | RC0805FR-0710K | 0,022 | 100 |  | 5 | RS | 0,002 € | 5 | 0,010
53 | 5 | 47R | 0805 | R6, R18, R25, R60, R66 | 2861899 | CRGCQ0805J47R | 0,007 | 10 | P47.0CCT-ND | 0,069 | 10 | 279-CRGCQ0805F47R | 0,028 | 10 | 223-0253 | CRG0805F47R | 0,016 | 50 | SMD0805-47R-1% | 0,022 | 100 |  | 5 | Farnell | 0,007 € | 5 | 0,033
54 | 2 | 100K | 0805 | R61, R65 | 2447551 | MCWR08X1003FTL | 0,010 | 10 | RMCF0805FT100KCT-ND | 0,024 | 10 | 71-CRCW0805100KFKEAC | 0,040 | 10 | 223-0691 | CRG0805F100K | 0,028 | 50 | 0805S8F1003T5E | 0,015 | 100 |  | 2 | Farnell | 0,010 € | 2 | 0,019
55 | 4 | 15R | 0805 | R7, R9, R11, R13 | 2447576 | MCWR08X15R0FTL | 0,008 | 10 | RNCP0805FTD15R0CT-ND | 0,063 | 10 | 652-CR0805FX-15R0ELF | 0,038 | 10 | 679-0914 | CRCW080515R0FKEA | 0,004 | 50 | 0805S8F150JT5E | 0,016 | 100 |  | 4 | RS | 0,004 € | 4 | 0,016
56 | 4 | DR1206-33R-4/8 | 1206 resistor array | RN1, RN2, RN5, RN6 | 1770128 | CAY16-330J4LF | 0,069 | 10 | CAY16-330J4LFCT-ND | 0,090 | 1 | 652-CAY16-330J4LF | 0,085 | 1 | 522-5670 | CAY16-330J4LF | 0,004 | 50 | 4D03WGJ0330T | 0,009 | 100 |  | 4 | RS | 0,004 € | 4 | 0,016
57 | 1 | DR1206-47K-4/8 | 1206 resistor array | RN3 | 2787793 | CAY16-4702F4LF | 0,178 | 10 | CAY16-473J4LF | 0,080 | 10 | 652-CAY16-473J4LF | 0,016 | 10 | 522-5759 | CAY16-473J4LF | 0,020 | 50 | 4D03WGJ0473T | 0,013 | 100 |  | 1 | TME | 0,013 € | 1 | 0,013
58 | 1 | 75031537 | Push-Pull Transformer | TR1 | 2907256 | 75031537 | 4,550 | 1 | 1297-1178-1-ND | 2,060 | 1 | 710-750315371 | 2,120 | 1 | 182-8977 | 750315371 | 2,560 | 1 | - |  |  |  | 1 | Digikey | 2,060 € | 1 | 2,060
59 | 4 | PESD12VL1BA,115 | SOD-323 | TVS1, TVS2, TVS3, TVS4 | 8737363 | PESD12VL1BA,115 | 0,365 | 5 | 1727-3808-1-ND | 0,320 | 10 | 771-PESD12VL1BA-T/R | 0,296 | 10 | 508-024 | PESD12VL1BA,115 | 0,294 | 20 | PESD12VL1BA.115 | 0,126 | 5 |  | 4 | TME | 0,126 € | 4 | 0,504
60 | 1 | 77317-104-28LF | THT, 28-pin 0.1" header right angled | X1 | - |  |  |  | S2111EC-14-ND | 1,030 | 1 | 649-77317-104-28LF | 1,540 | 1 | - |  |  |  | - |  |  | 1 |  | Digikey | 1,030 € | 1 | 1,030
61 | 1 | 691327310016 | THT, 16-pin 3.81mm terminal block header, male pins | X3 | 1793077 | MCD 1,5/ 8-G1-3,81 | 5,770 | 1 | 732-691327310016-ND | 7,810 | 1 | 651-1843130 | 9,270 | 1 | 191-1724 | 691327310016 | 7,900 | 1 | - |  |  | 1 |  | Farnell | 5,770 € | 1 | 5,770
62 | 1 | 691322310008 | THT, 8-pin 3.81mm terminal block header, male pin | X4 | 1705378 | EB3-08-B | 2,250 | 1 | 732-2093-ND | 1,360 | 1 | 710-691322310008 | 1,400 | 1 | 824-6661 | 691322310008 | 1,470 | 1 | 15EDGRC-3.81-08P-14-00A(H) | 0,651 | 1 | 1 |  | TME | 0,651 € | 1 | 0,651
63 | 2 | DS1014-10RF1B | THT, 10-pin IDC Socket 2mm, angled 90° | X5, X6 | - |  |  |  | - |  |  | - |  |  | - |  |  |  | DS1014-10RF1B | 0,220 | 3 | 2 |  | TME | 0,220 € | 2 | 0,440
64 | 2 | DS1023-2*14S21 | THT, 28-pin 2.54 mm 2x14 receptacle | X7, X8 | 3570684 | SSQ-114-01-T-D | 2,680 | 1 | SAM1183-14-ND | 2,070 | 1 | 200-SSQ11401TD | 2,130 | 1 | 207-9041 | SSQ-114-01-T-D | 2,820 | 1 | DS1023-2*14S21 | 0,326 | 2 | 2 |  | TME | 0,326 € | 2 | 0,651
65 | 1 | LF XTAL026392 | 16 MHz XTAL; 7.5x5.1x1.4mm | Y1 | 1276696 | LFXTAL026392 | 1,250 | 1 | 1923-1009-ND | 0,850 | 1 | 449-LFXTAL026392BULK | 0,972 | 1 | 148-4357 | LFXTAL026392 | 0,960 | 10 | 16.00M-12SM | 0,950 | 1 |  | 1 | Digikey | 0,850 € | 1 | 0,850
66 | 2 | SMAJ16 | SMA | ZD1, ZD2 | 3577011 | SMAJ16A-13-F | 0,104 | 5 | SMAJ16A-FDICT-ND | 0,400 | 1 | 621-SMAJ16A-13-F | 0,356 | 1 | 171-9586 | SMAJ16A | 0,149 | 25 | SMAJ16A-13-F |  | 5 |  | 2 | Farnell | 0,104 € | 2 | 0,208
 |  |  |  |  |  |  |  |  |  |  |  |  |  |  |  |  |  |  |  |  |  | 10 | 222 |  |  |  | 60,80 €
 |  | Not installed
 | 1 | N.C. | 0603 | C1 |  |  |  |  |  |  |  |  |  |  |  |  |  |  |  |  |  |  | 1 | Farnell | 0,000 € | 1 | 0,000
 | 2 | N.C. | 0805 | C88, C89
 | 1 | N.C. | 0805 | C24 |  |  |  |  |  |  |  |  |  |  |  |  |  |  |  |  |  |  | 1 | Farnell | 0,000 € | 1 | 0,000
 | 4 | N.C. |  | D11, D12, D13, D14 |  |  |  |  |  |  |  |  |  |  |  |  |  |  |  |  |  |  | 4 | Farnell | 0,000 € | 4 | 0,000
 | 1 | N.C. |  | IC9 |  |  |  |  |  |  |  |  |  |  |  |  |  |  |  |  |  |  | 1 | Farnell | 0,000 € | 1 | 0,000
 | 1 | 503398-1892 | Micro SD, push-push, 8-pin | J2 | 2358234 | 503398-1892 | 1,980 | 1 | WM11190CT-ND | 2,160 | 1 | 538-503398-1892 | 1,960 | 1 | 880-1277 | 503398-1892 | 2,600 | 1 | MX-503398-1892 | 0,860 | 2 |  | 1 | TME | 0,860 € | 1 | 0,860
 | 3 | N.C. | 0805 | R3, R8, R12 |  |  |  |  |  |  |  |  |  |  |  |  |  |  |  |  |  |  | 3 | Farnell | 0,000 € | 3 | 0,000
 | 1 | N.C. | 0805 | RN4 |  |  |  |  |  |  |  |  |  |  |  |  |  |  |  |  |  |  | 1 | Farnell | 0,000 € | 1 | 0,000
 | 1 | N.C. |  | X2 |  |  |  |  |  |  |  |  |  |  |  |  |  |  |  |  |  |  | 1 | Farnell | 0,000 € | 1 | 0,000
 |  | Related parts and accessories
 | 2 | PMB-1 | PCB bracket; polyamide | KK1, KK2 | - |  |  |  | - |  |  | - |  |  | - |  |  |  | PMB-1 | 0,072 | 10 |  |  | TME | 0,072 € | 2 | 0,145
 | 2 | JUMPER-2.0/R | 2mm jumper |  |  |  |  |  |  |  |  |  |  |  |  |  |  |  | JUMPER-2.0/R | 0,045 | 20 |  |  | TME | 0,045 € | 2 | 0,089
 | 4 | TJ0831530000G | 8-pin 3.81mm pluggable terminal block |  | 2579776 | EBK-08-B | 2,400 | 1 | 609-3803-ND | 1,760 | 1 | 649-220004-D081B01LF | 1,530 | 1 | - |  |  |  | 15EDGK-3.81-08P-14-00A(H) | 1,430 | 1 |  |  | TME | 1,430 € | 4 | 5,720
 |  |  |  |  |  |  |  |  |  |  |  |  |  |  |  |  |  |  |  |  |  |  |  |  |  |  | 5,95 €
 |  | Custom made components
 | 1 | PCB 4-layer 146 x 95 mm |  | - |  |  |  |  |  |  |  |  |  |  |  |  |  |  |  |  |  |  |  | JLCPCB | 11,374 € | 1 | 11,374
 |  |  |  |  |  |  |  |  |  |  |  |  |  |  |  |  |  |  |  |  |  |  |  |  |  |  | 11,37 €
 |  |  | All prices are net prices (without VAT)
 |  |  |  |  |  |  |  |  |  |  |  |  |  |  |  |  |  |  |  |  |  |  |  |  |  | Total | 78,12 €
 |  |  | Please note that BOM does not contain ordering number for parts on reels or that which includes re-reeling fee (e.g. Farnell). Take also into account that total cost is higher because min. quantity (MOQ) for many parts is larger then what is needed for single unit.
 |  |  | All resistors are 1% 0805 and all capacitors are X7R 0805 if not otherwise specified.

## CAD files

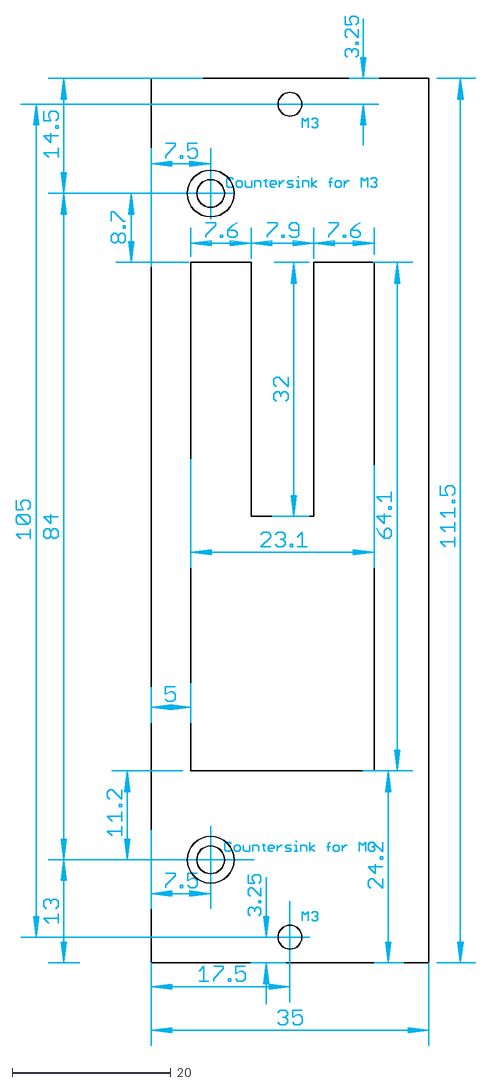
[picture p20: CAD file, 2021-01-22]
Mechanical/MIO168 r2B3 front panel.dxf
58.0 x 129.8

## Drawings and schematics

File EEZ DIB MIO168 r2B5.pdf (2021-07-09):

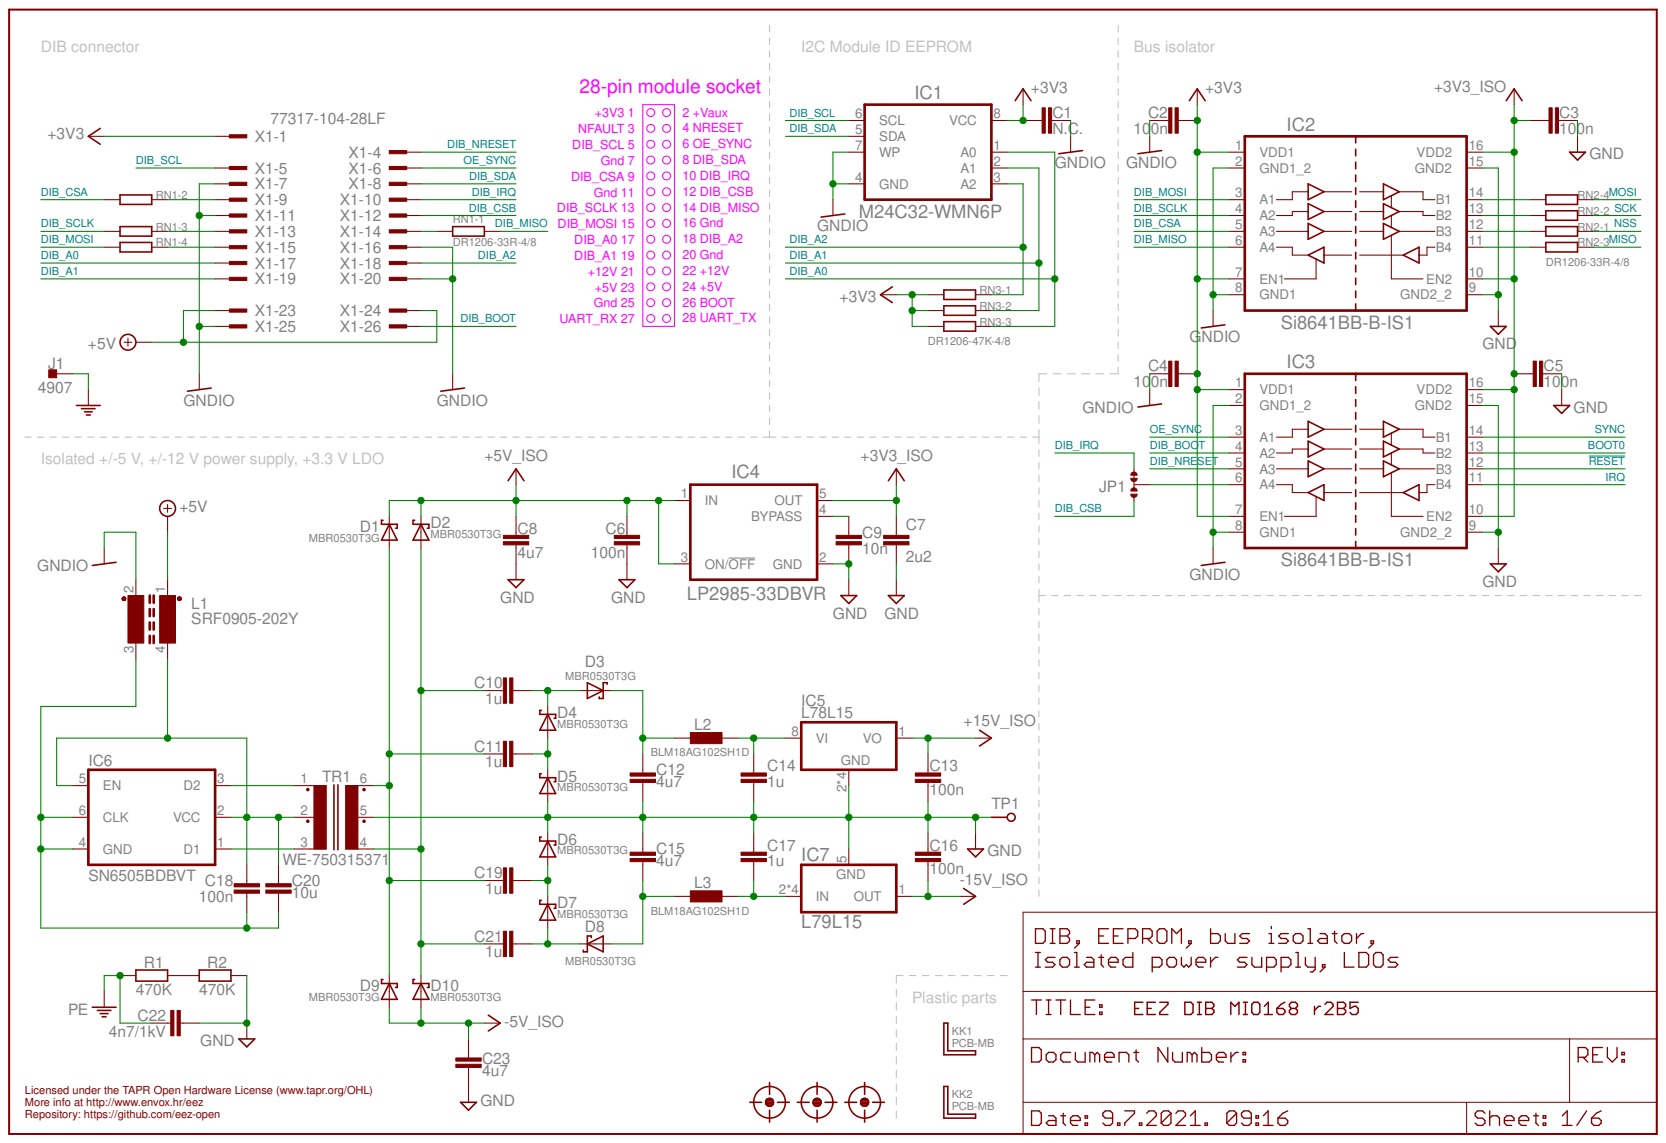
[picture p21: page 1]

Isolated +/-5 V, +/-12 V power supply, +3.3 V LDO

Licensed under the TAPR Open Hardware License (www.tapr.org/OHL) Repository: https://github.com/eez-open More info at http://www.envox.hr/eez

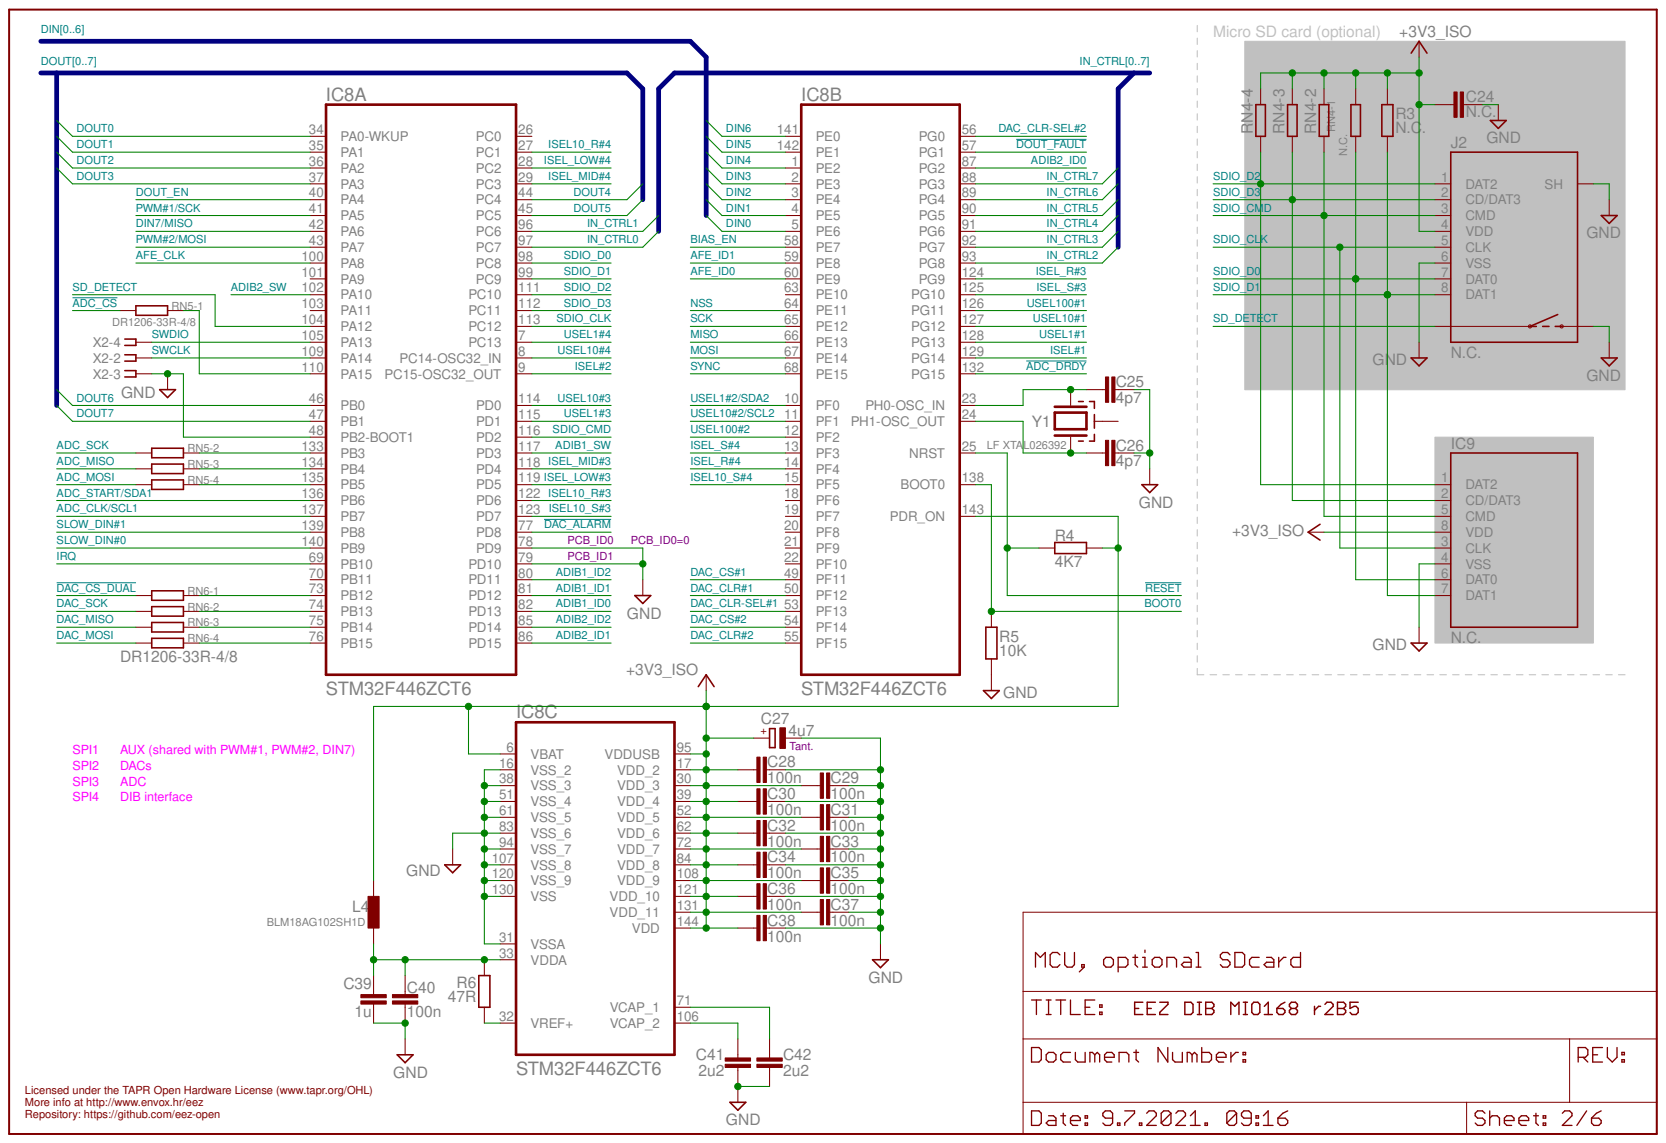
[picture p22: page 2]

Micro SD card (optional)

SCK MISO MOSI NSS

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

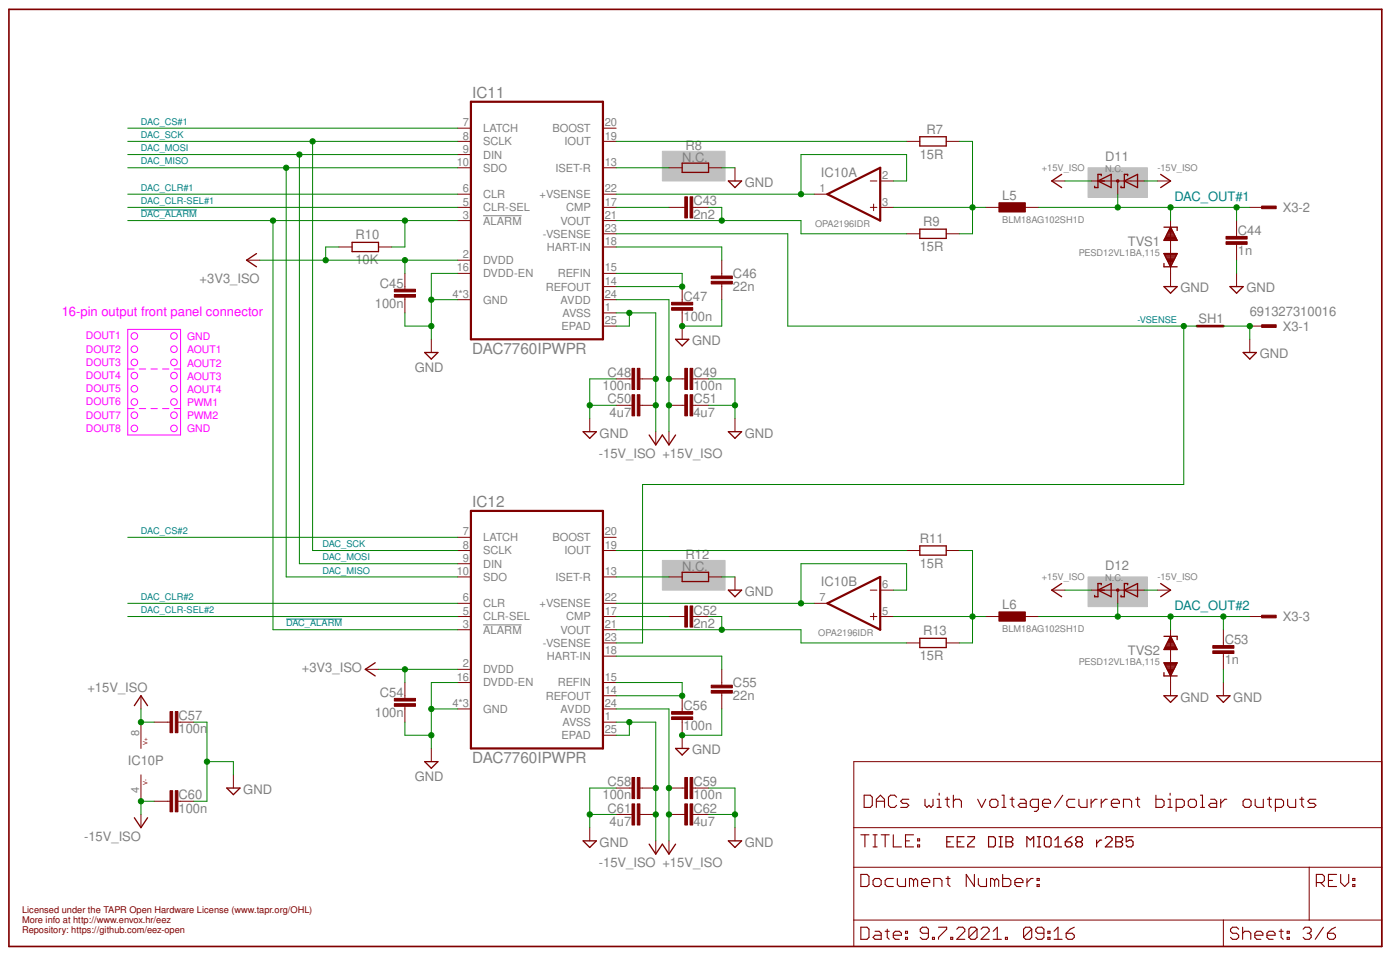
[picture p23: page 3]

16-pin output front panel connector GND

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

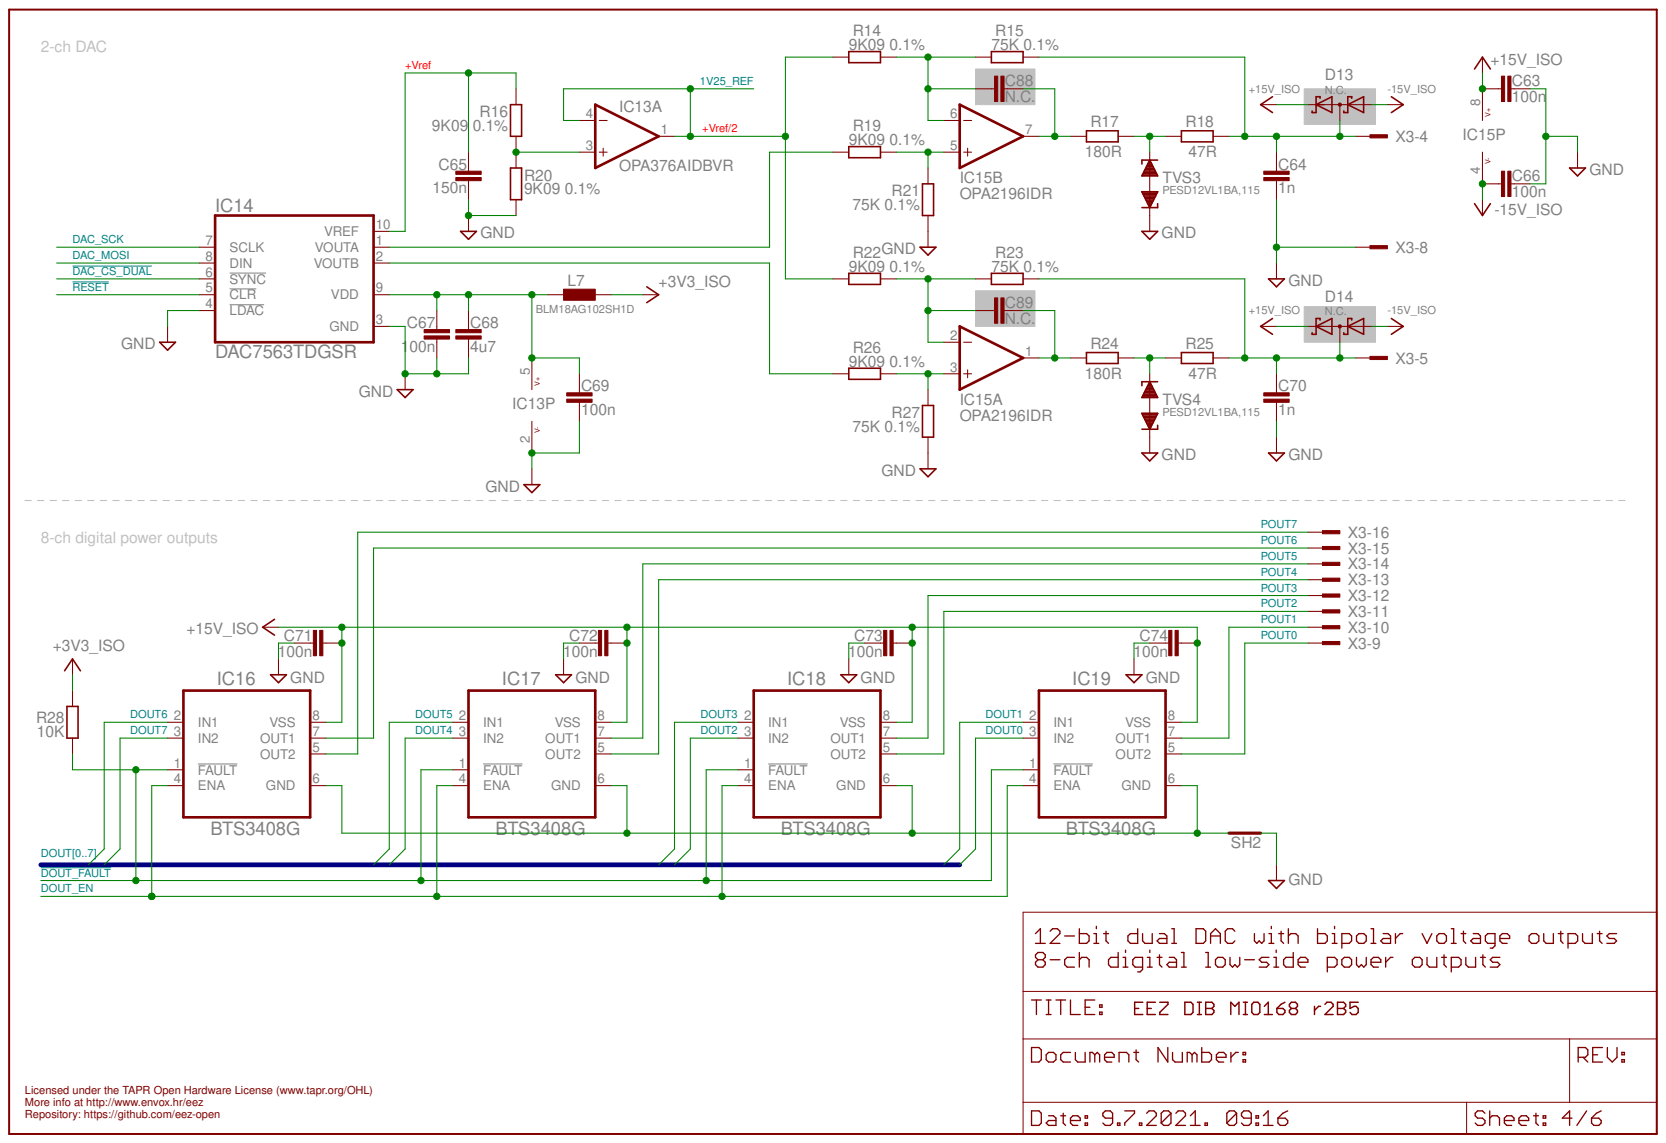
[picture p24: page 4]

+Vref/2 | N.C.

3 | GND

8-ch digital power outputs

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

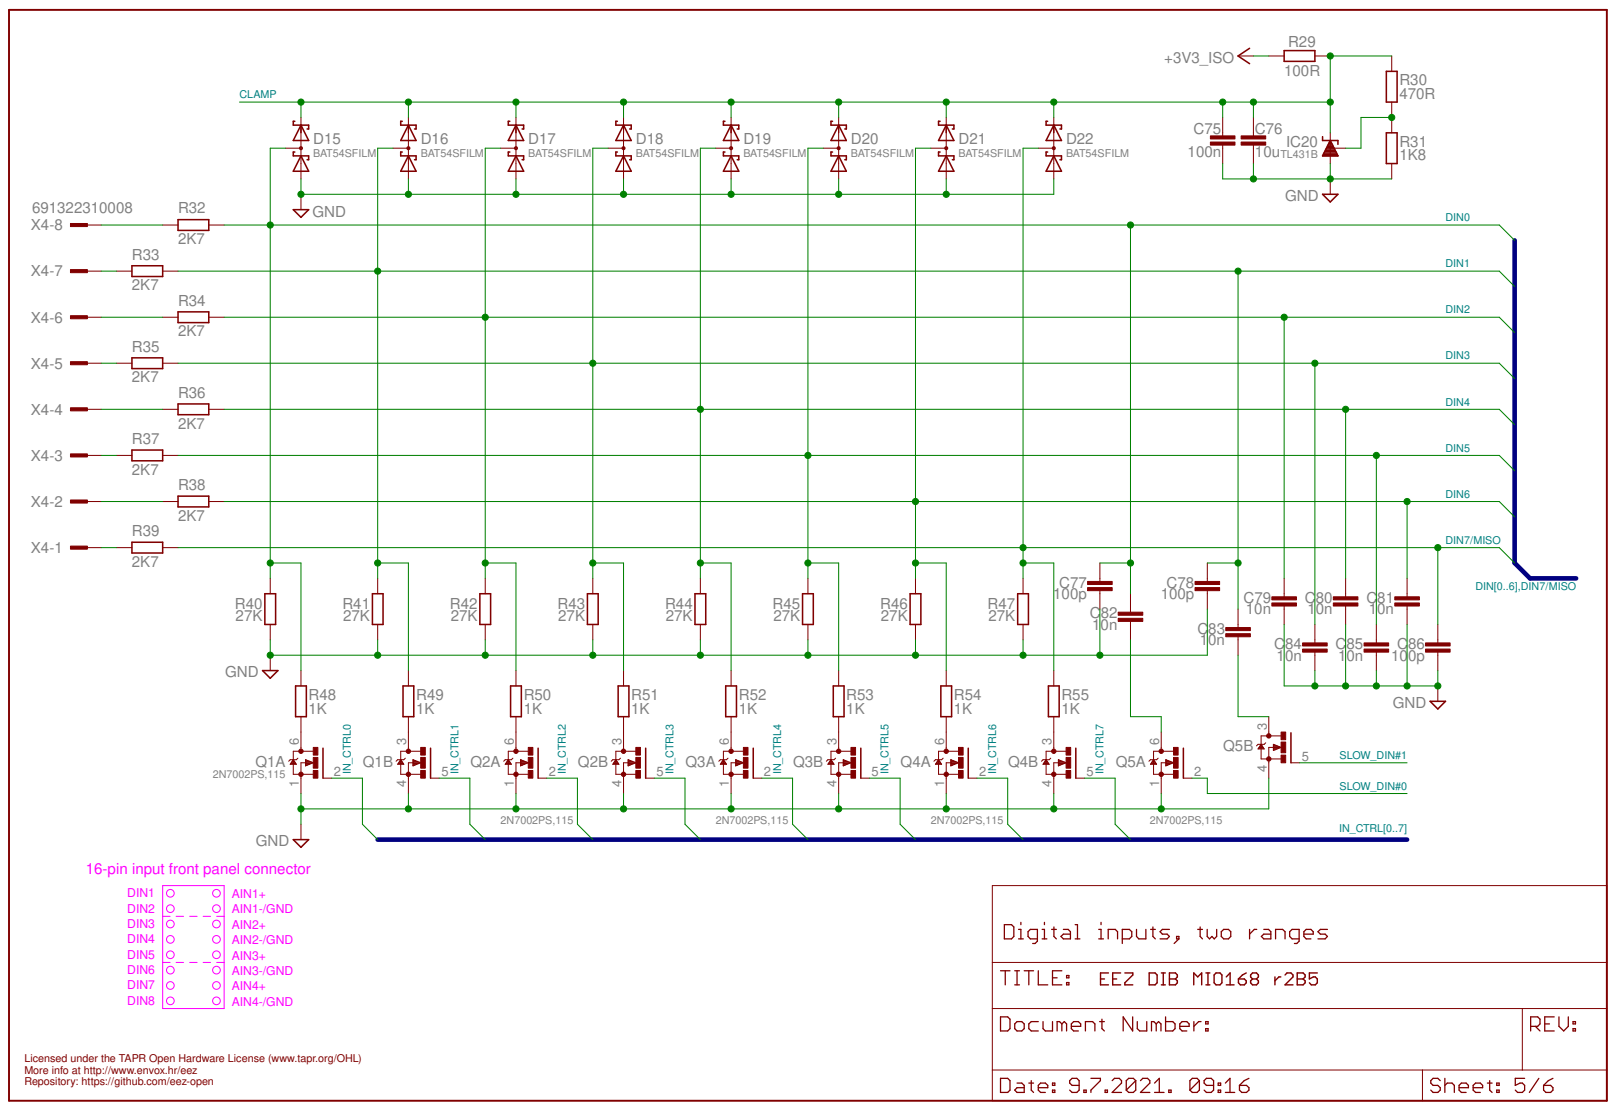
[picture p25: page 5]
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

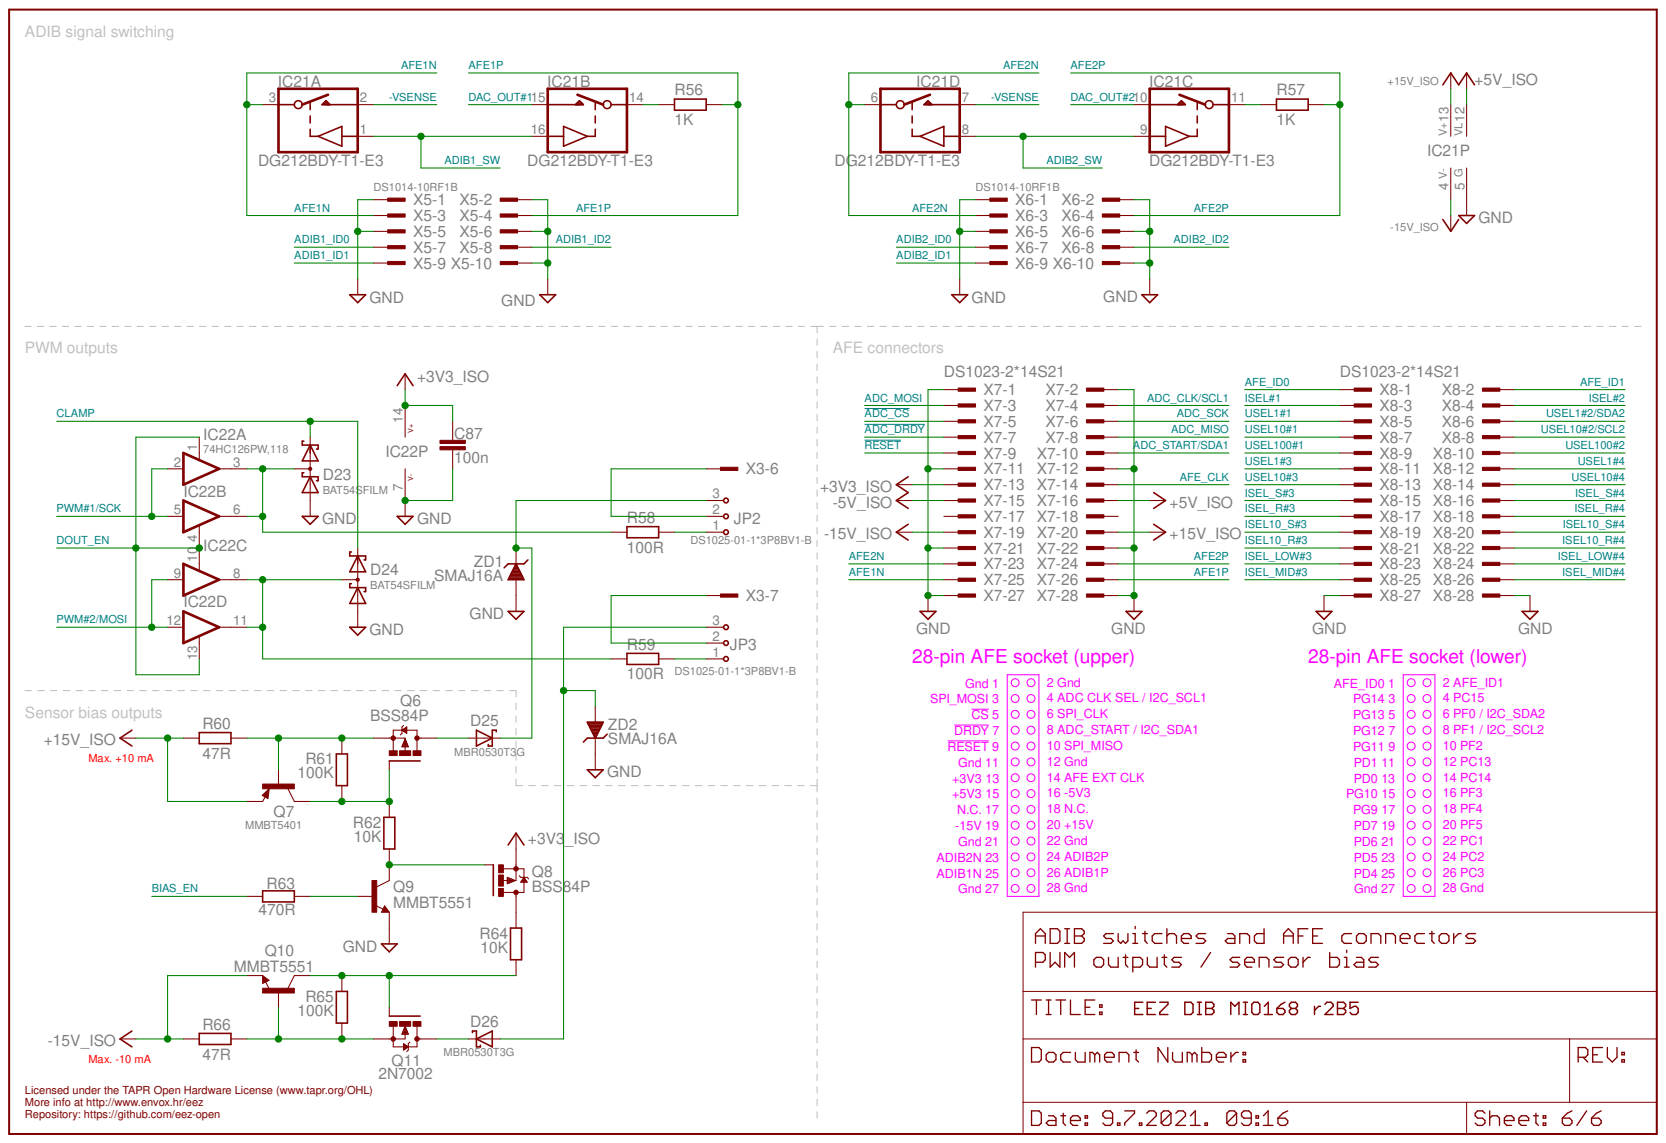
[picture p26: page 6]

28-pin AFE socket (upper)

GND
28-pin AFE socket (lower)

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

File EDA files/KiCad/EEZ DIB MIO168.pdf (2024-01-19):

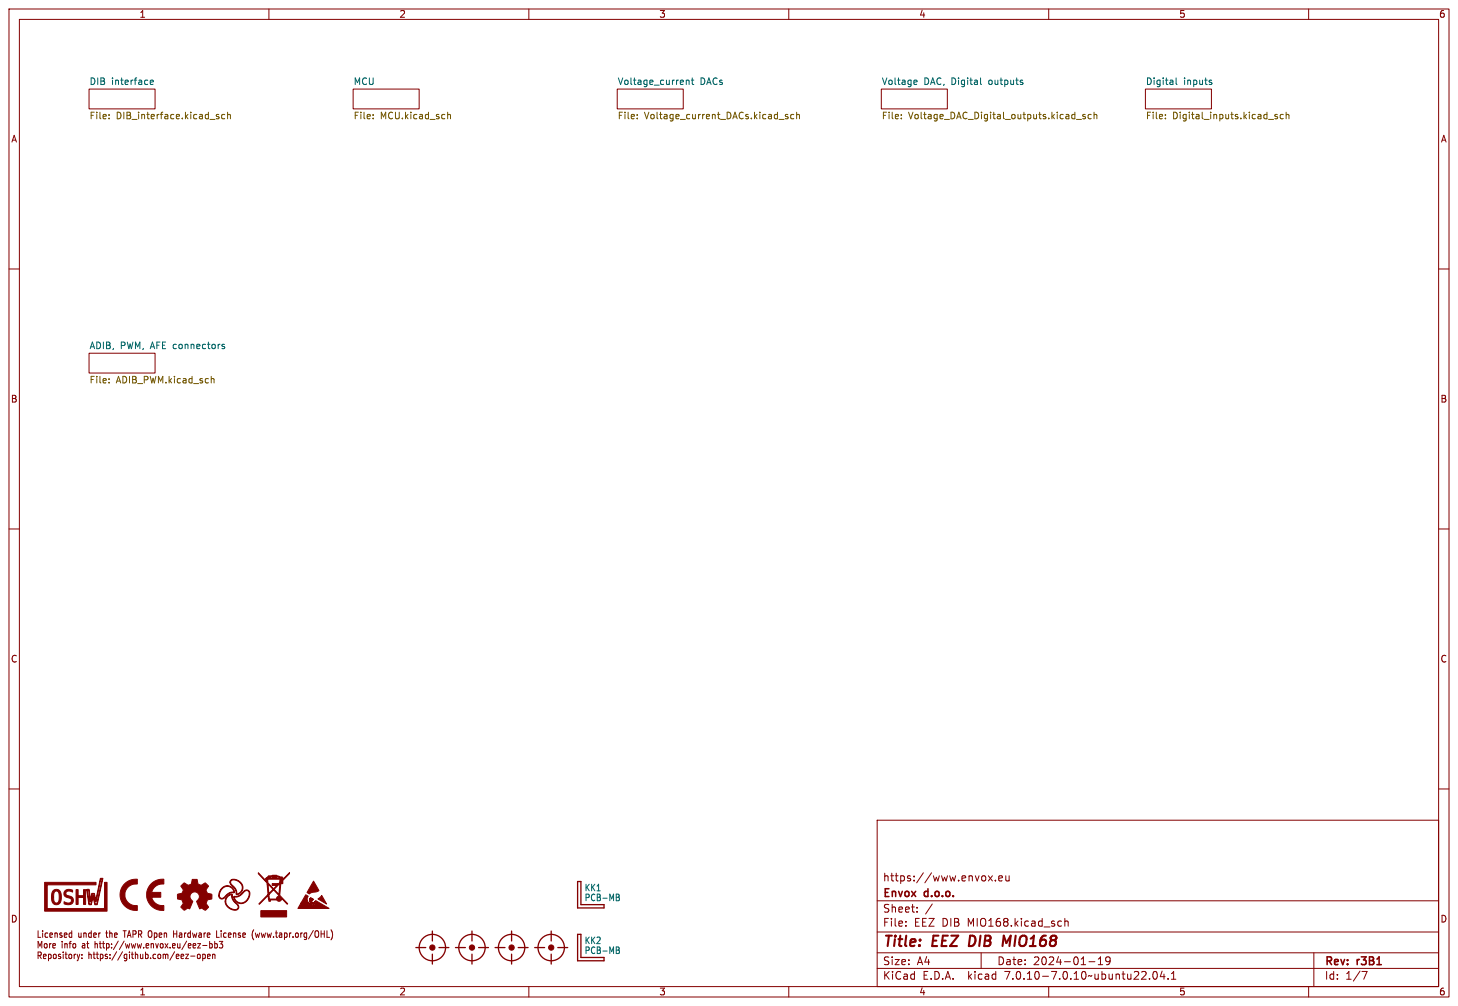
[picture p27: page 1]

Voltage DAC, Digital outputs File: Voltage_DAC_Digital_outputs.kicad_sch

Licensed under the TAPR Open Hardware License (www.tapr.org/OHL) More info at http://www.envox.eu/eez-bb3

Id: 1/7 Title: EEZ DIB MIO168

Repository: https://github.com/eez-open

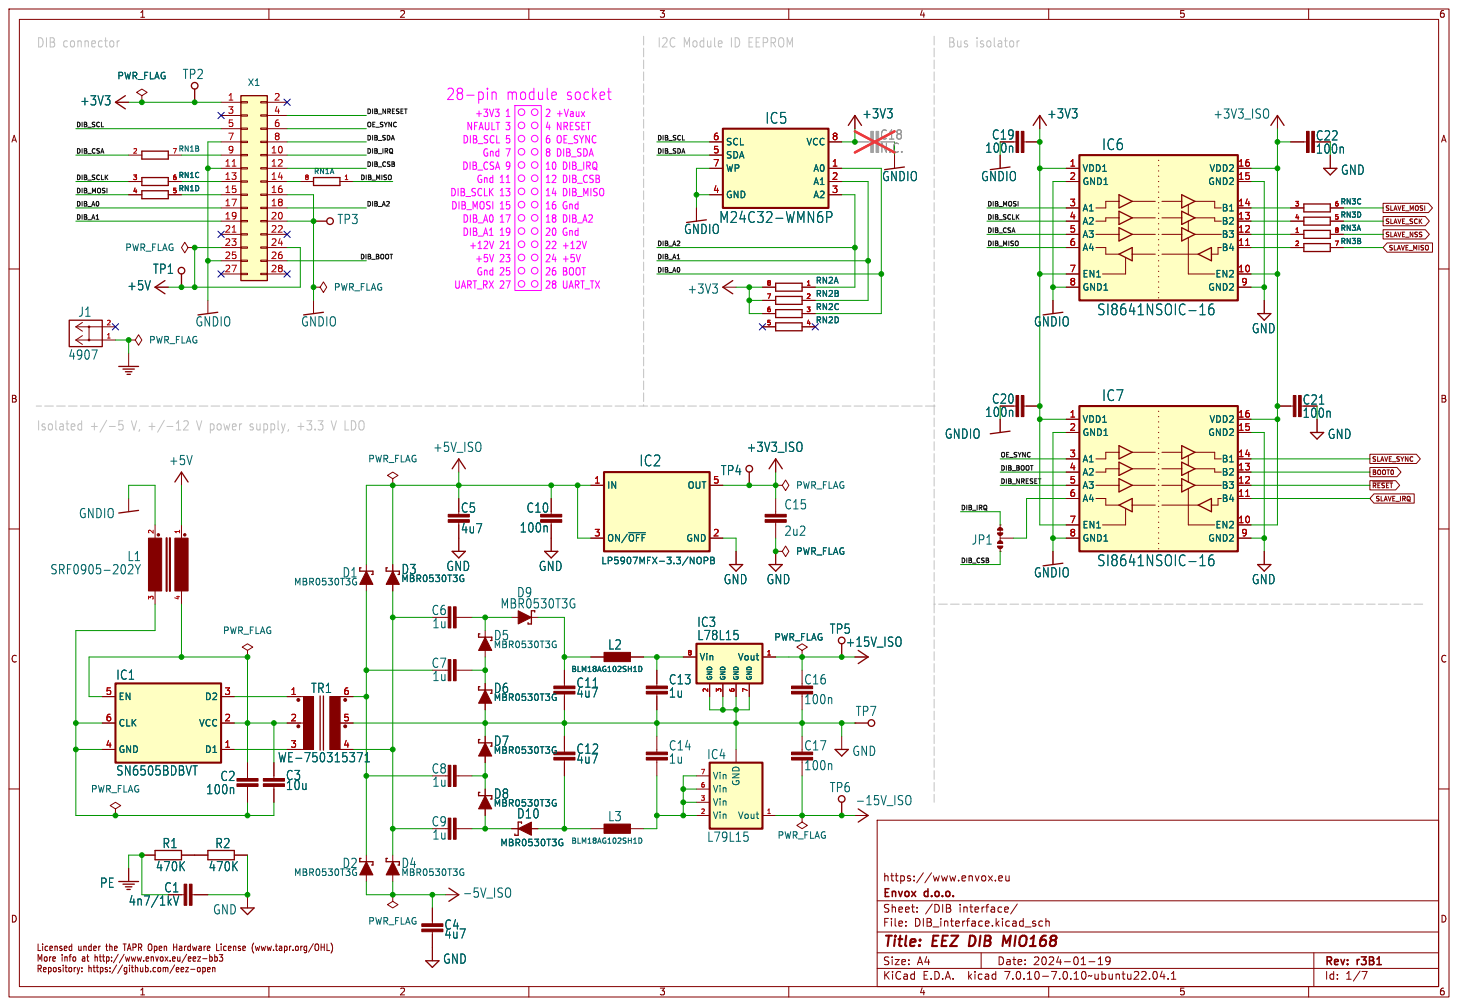
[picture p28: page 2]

2 +Vaux 16 Gnd Gnd 7 DIB_SCL 5 +3V3 1 Gnd 11 DIB_CSA 9
NFAULT 3 UART_RX 27 Gnd 25 +5V 23 DIB_A1 19 DIB_A0 17 +12V 21

Id: 1/7 Title: EEZ DIB MIO168

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

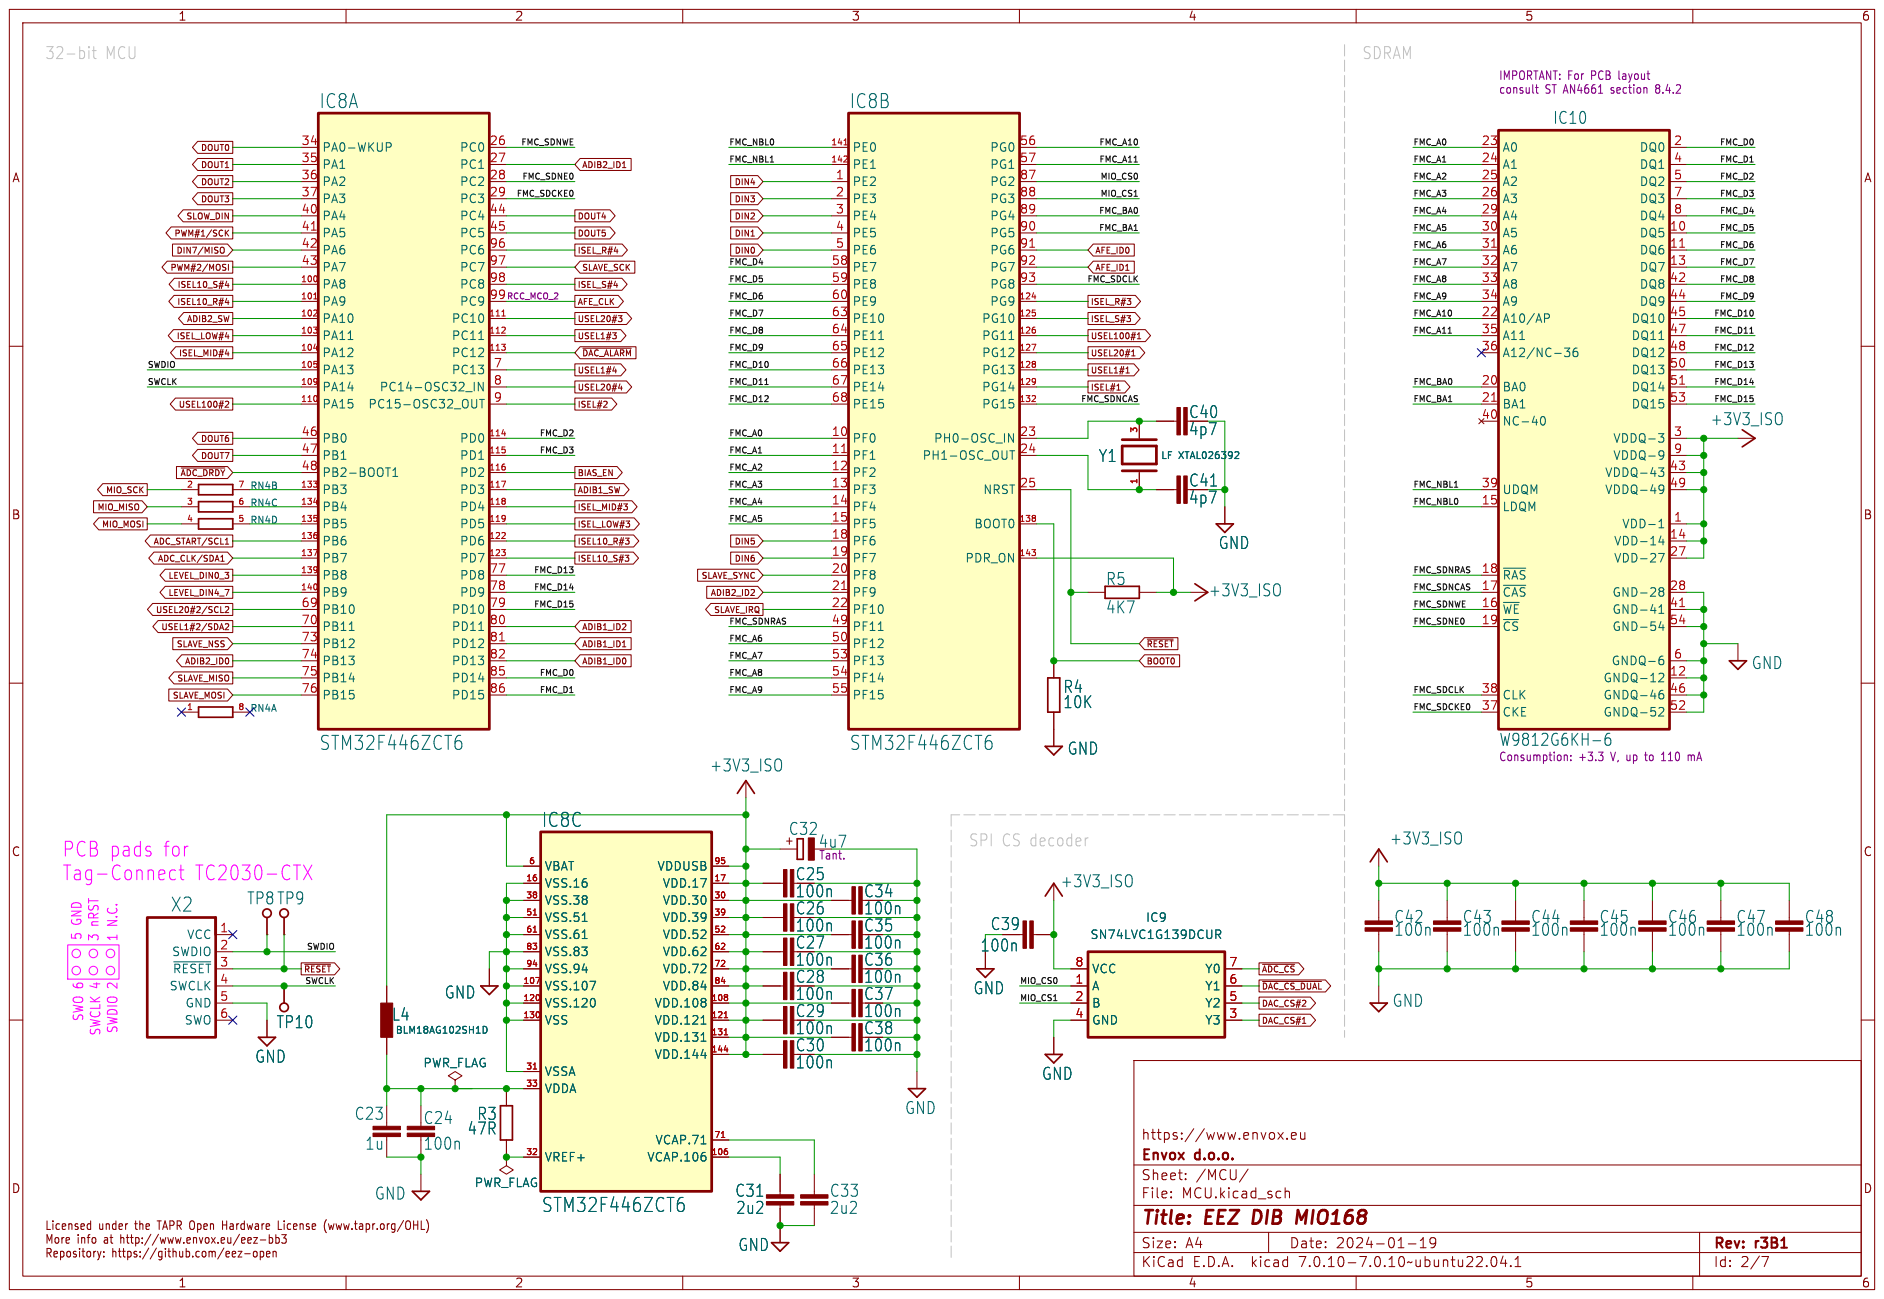
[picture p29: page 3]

IMPORTANT: For PCB layout consult ST AN4661 section 8.4.2 SWO 6

DIN0 DOUT1 PWM#2/MOSI PWM#1/SCK DIN7/MISO

SPI CS decoder Licensed under the TAPR Open Hardware License (www.tapr.org/OHL) More info at http://www.envox.eu/eez-bb3

Repository: https://github.com/eez-open SWDIO 2 SWCLK 4

File: MCU.kicad_sch Sheet: /MCU/ Envox d.o.o. https://www.envox.eu

Id: 2/7 Title: EEZ DIB MIO168

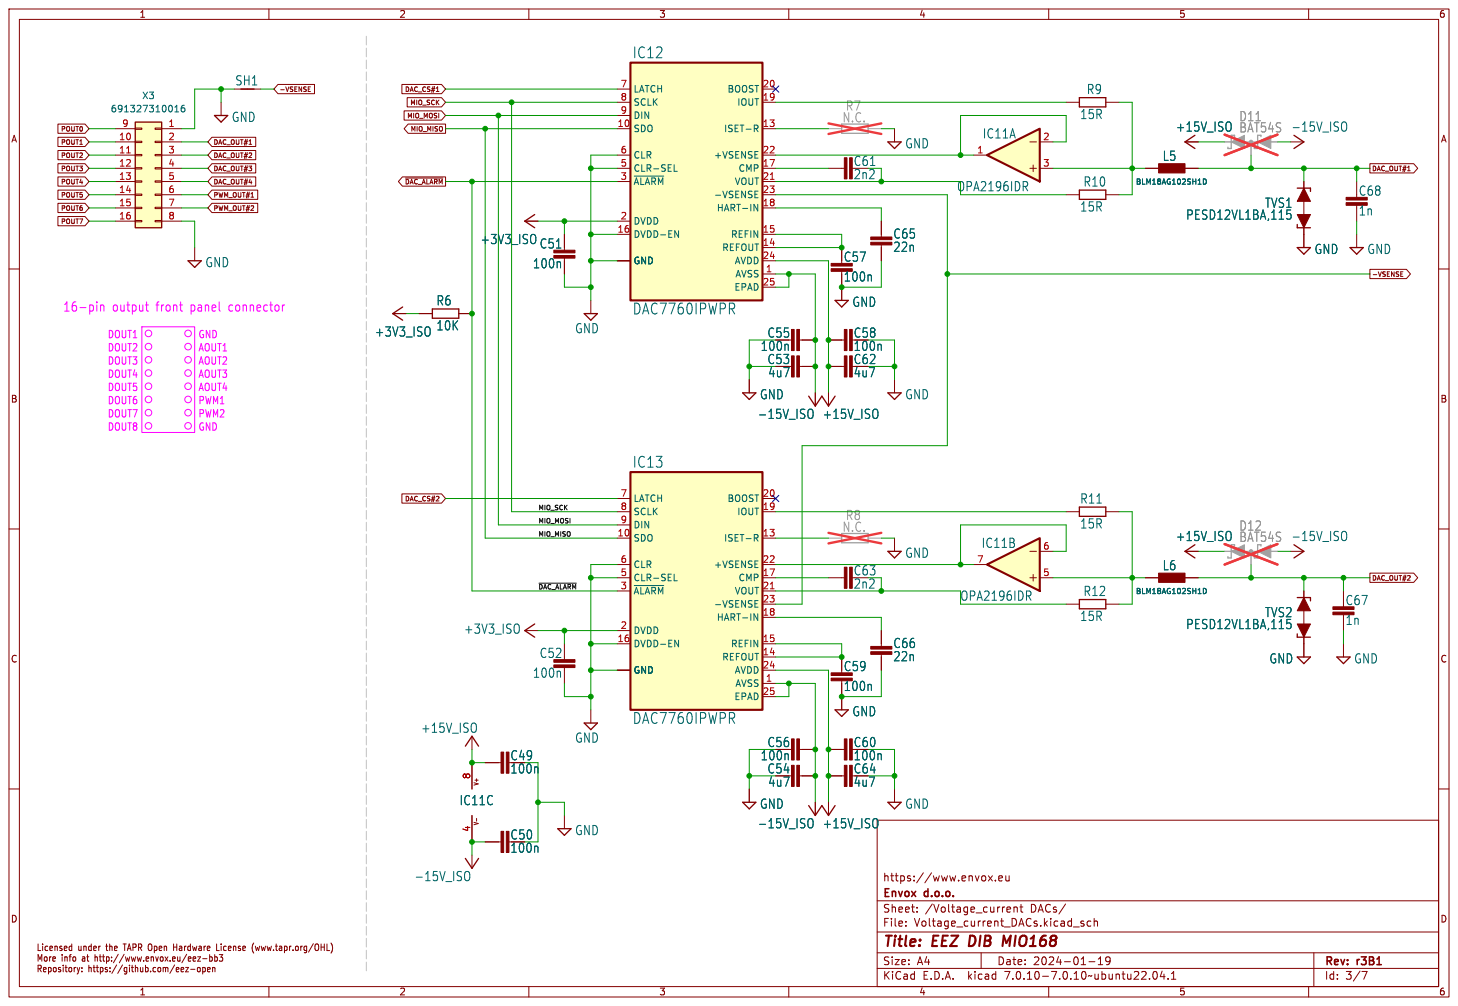
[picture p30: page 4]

Id: 3/7 Title: EEZ DIB MIO168

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

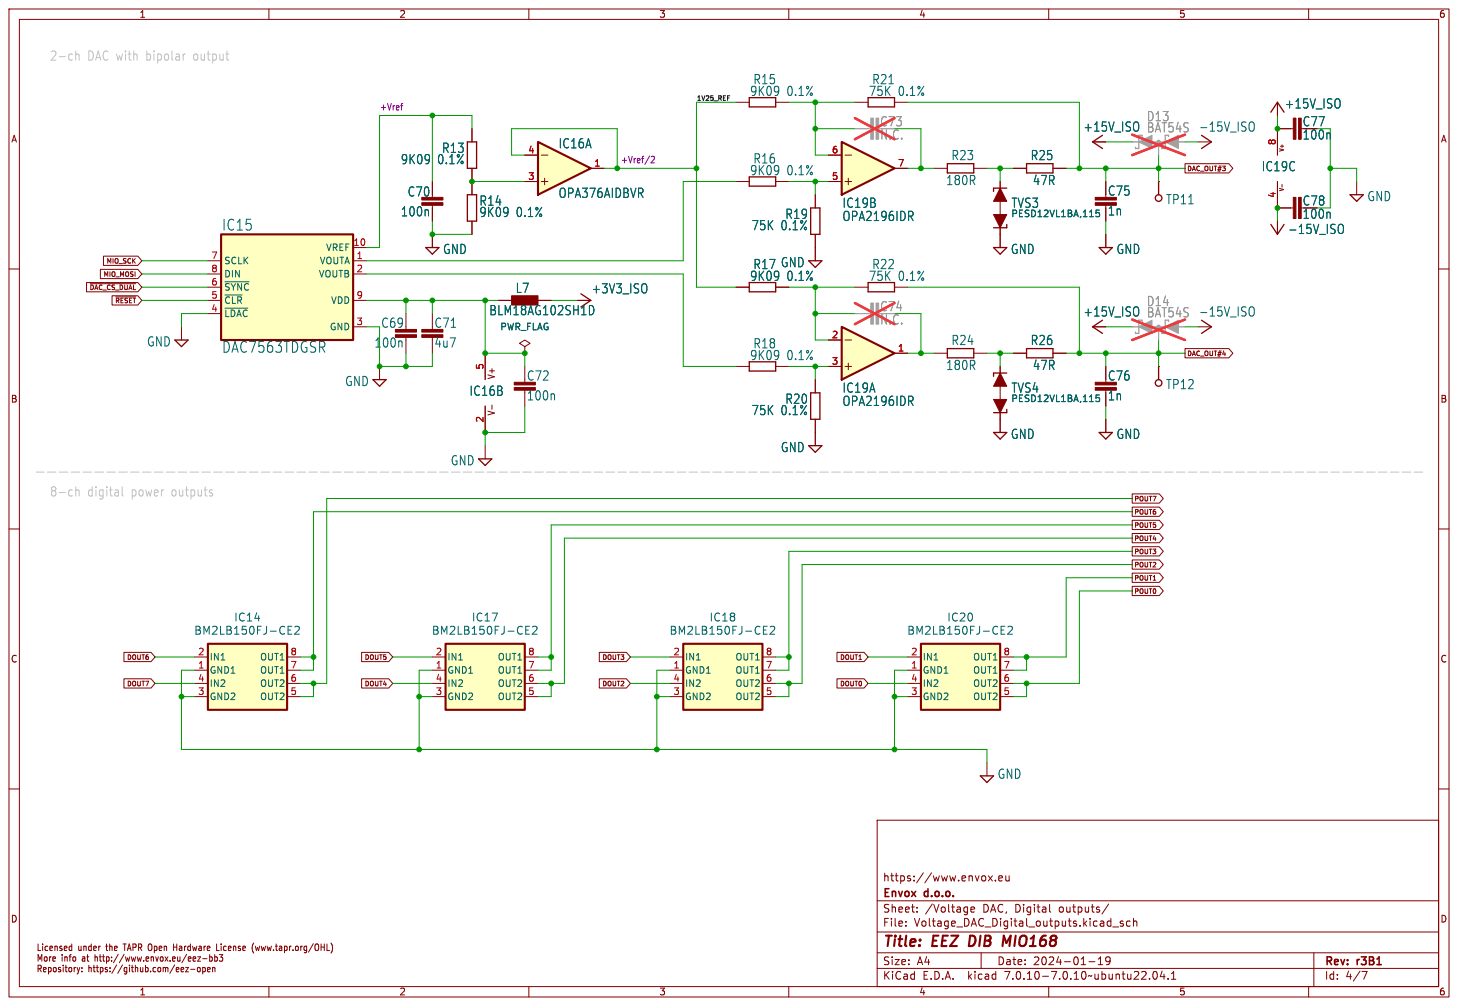
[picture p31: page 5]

1V25_REF 2-ch DAC with bipolar output

8-ch digital power outputs

Id: 4/7 Title: EEZ DIB MIO168

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

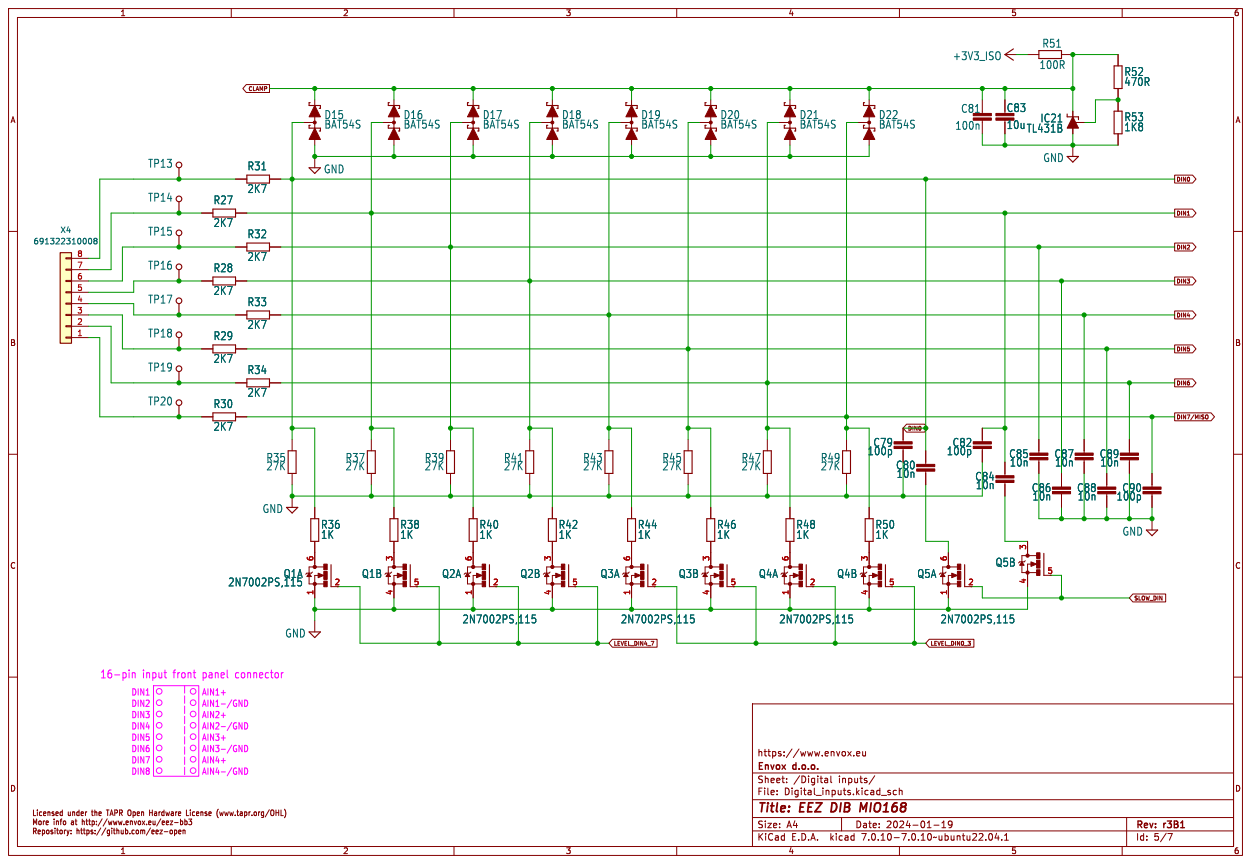
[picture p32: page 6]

Id: 5/7 Title: EEZ DIB MIO168

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


Id: 6/7 Title: EEZ DIB MIO168

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





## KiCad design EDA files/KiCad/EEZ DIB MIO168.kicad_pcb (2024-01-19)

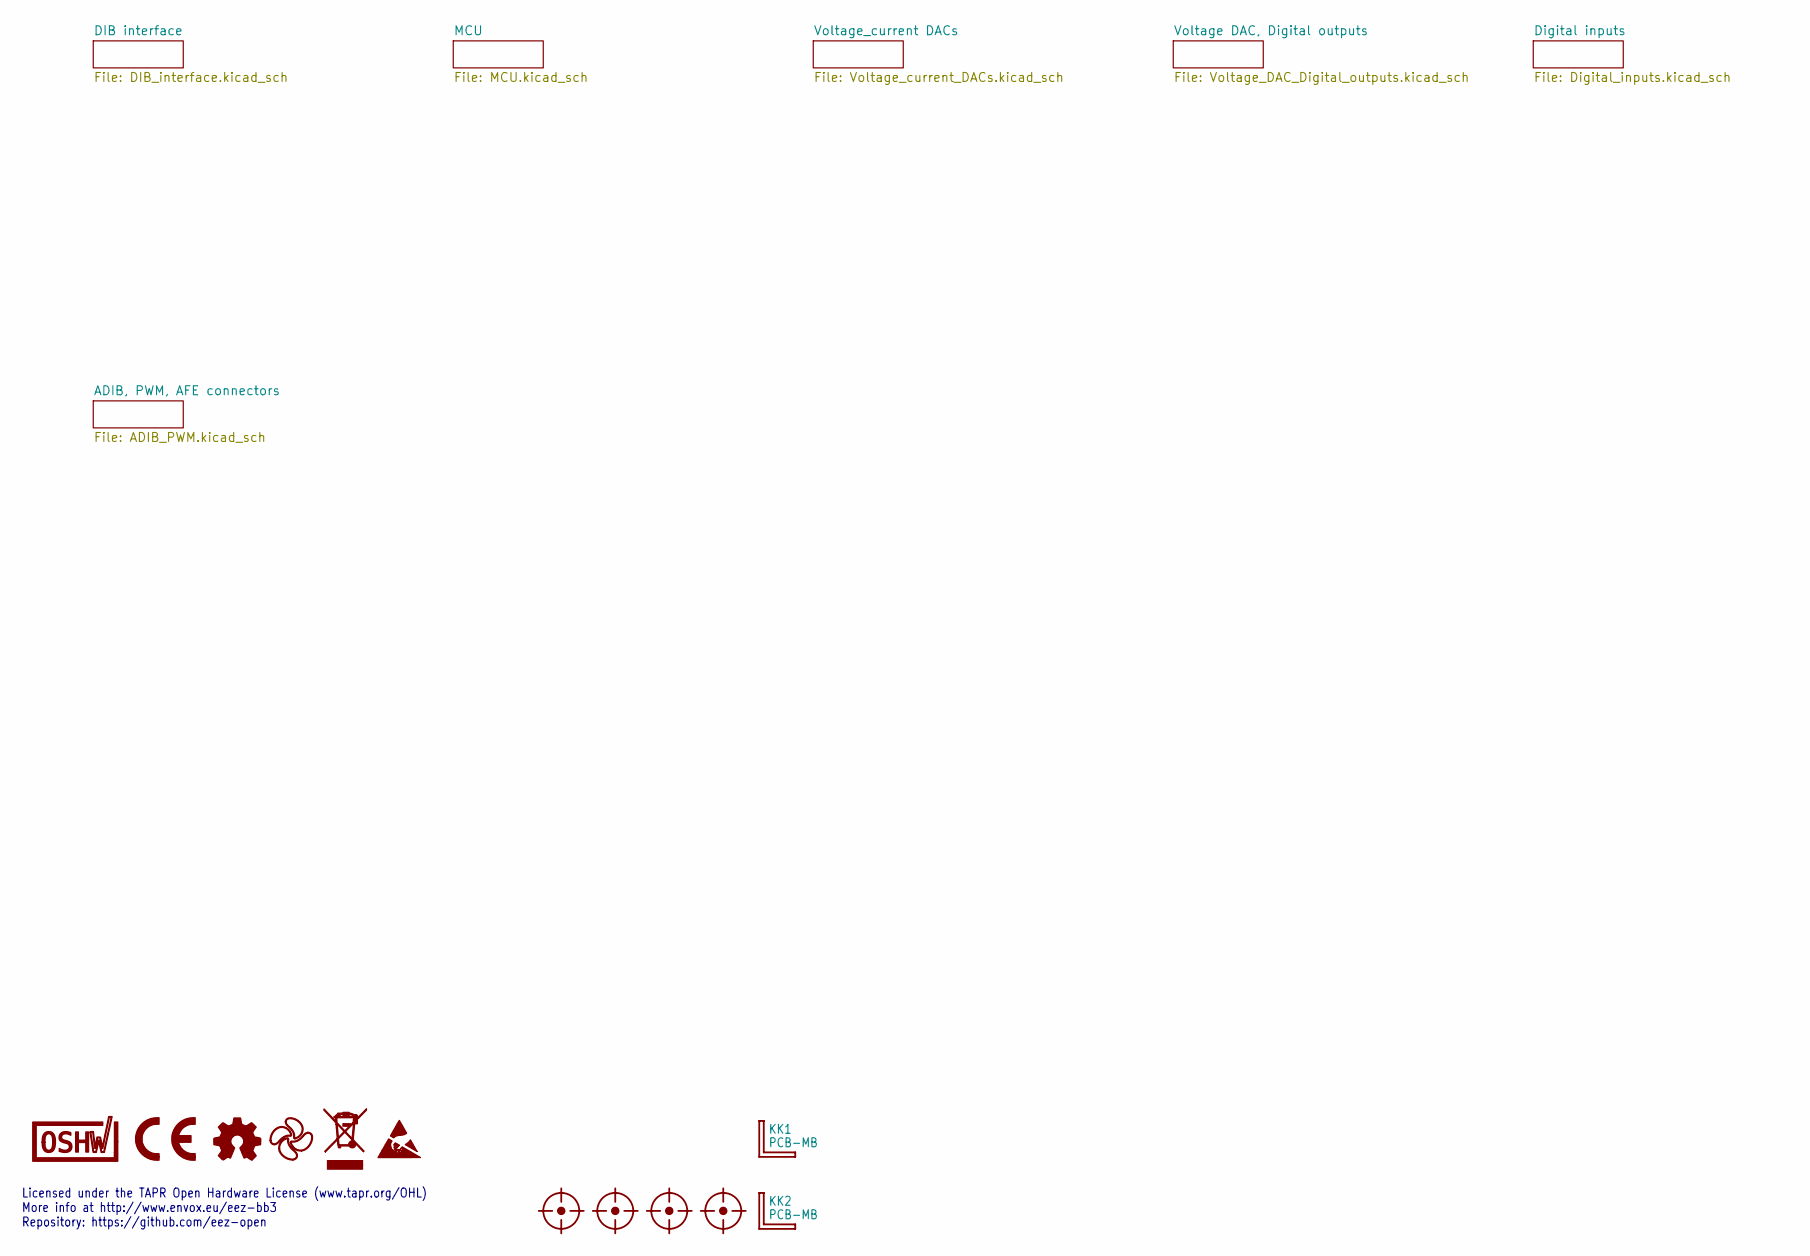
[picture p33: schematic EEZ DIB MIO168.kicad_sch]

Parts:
FM1, FM2, FM3, FM4: FIDUCIAL_2; Fiducial
KK1, KK2: PCB-MB; PCB-MB-01; DigiKey RPC1760-ND
LOGO1: OSHWA logo; OSHWA logo (9.5 x 5 mm)
LOGO2: CR logo; CE logo
LOGO3: Open HW logo
LOGO4: EEZ logo; EEZ logo (outline 6mm)
LOGO5: WEEE logo
LOGO6: ESD logo

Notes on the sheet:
Licensed under the TAPR Open Hardware License (www.tapr.org/OHL) More info at http://www.envox.eu/eez-bb3 Repository: https://github.com/eez-open

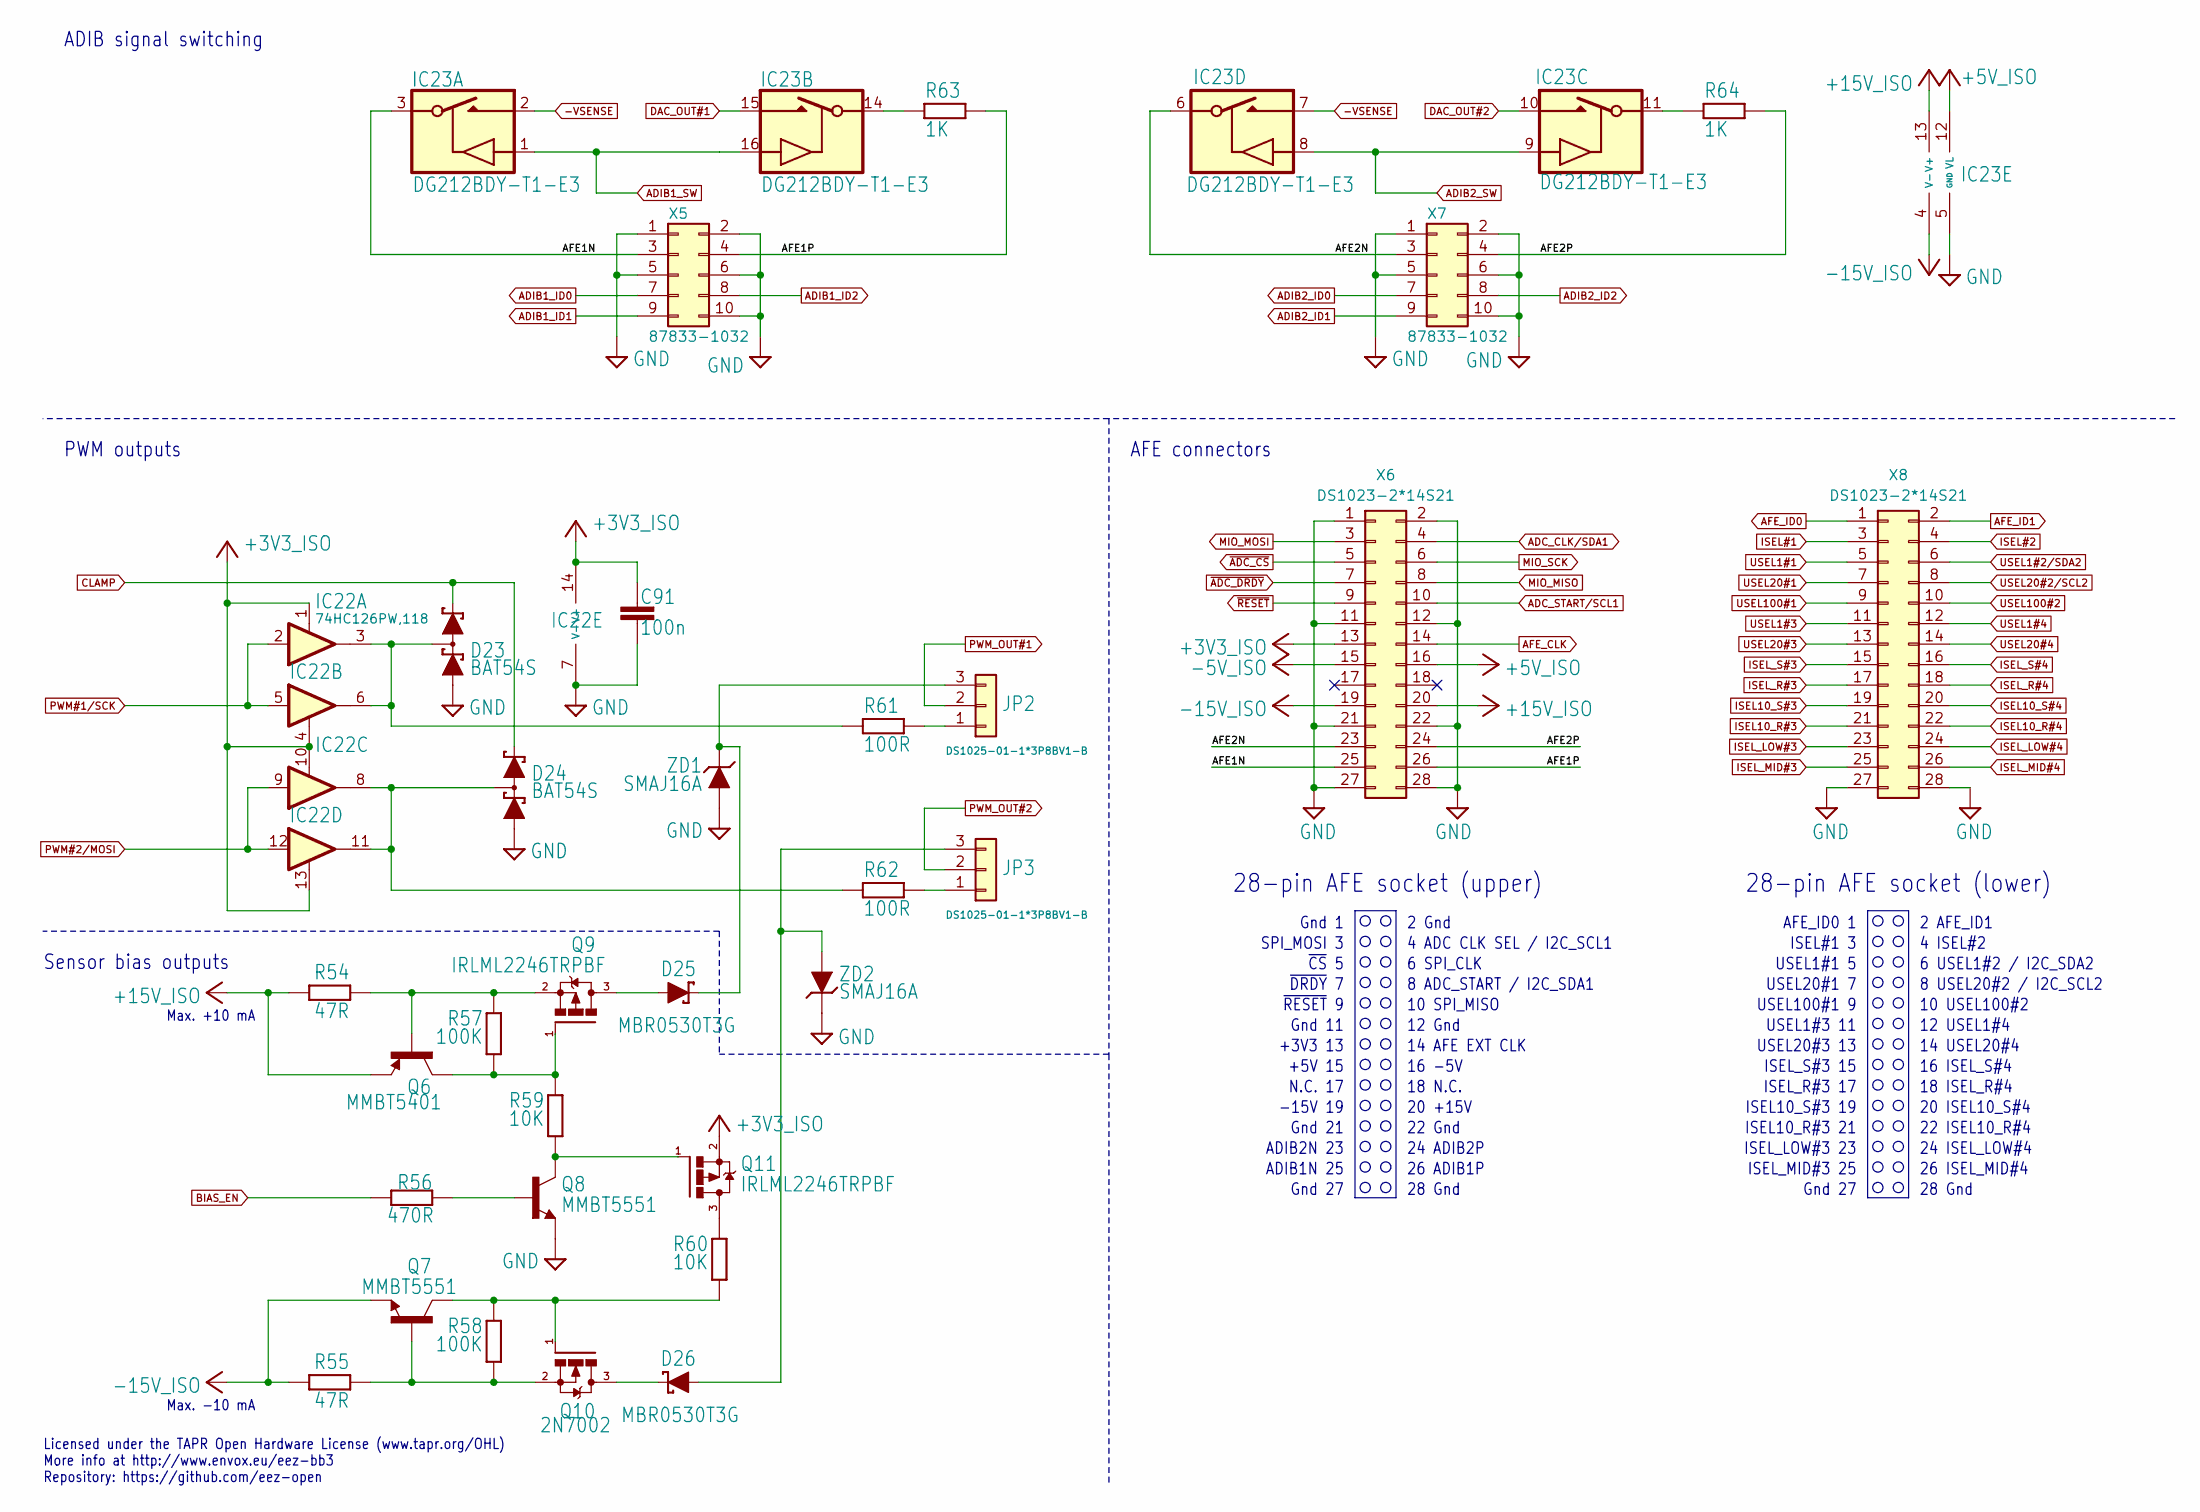
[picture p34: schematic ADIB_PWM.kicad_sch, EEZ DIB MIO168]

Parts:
C91: 100n; C_0603_1608Metric; DigiKey 1276-1005-2-ND
D23, D24: BAT54S; SOT23-3; DigiKey 497-2522-1-ND
D25, D26: MBR0530T3G; SOD123; DigiKey 863-MBR0530T3G
IC22: 74HC126PW,118; PW(R-PDSO-G14); DigiKey 1727-6579-1-ND
IC23: DG212BDY-T1-E3; SO16; DigiKey DG212BDY-T1-E3CT-ND
JP2, JP3: DS1025-01-1*3P8BV1-B; ZL303-03P; DigiKey 952-1312-ND
Q6: MMBT5401; SOT23-BEC; DigiKey MMBT5401-FDICT-ND
Q7, Q8: MMBT5551; SOT23-BEC; DigiKey MMBT5551LT1GOSCT-ND
Q9, Q11: IRLML2246TRPBF; SOT103P240X110-3N; DigiKey IRLML2246TRPBFTR-ND
Q10: 2N7002; SOT103P240X110-3N; DigiKey 2N7002LT1GOSCT-ND
R54, R55: 47R; R_0805_2012Metric; DigiKey P47.0CCT-ND
R56: 470R; R_0805_2012Metric; DigiKey 311-470CRCT-ND
R57, R58: 100K; R_0805_2012Metric; DigiKey RMCF0805FT100KCT-ND
R59, R60: 10K; R_0805_2012Metric; DigiKey CRGH0603F10K
R61, R62: 100R; R_0805_2012Metric; DigiKey 311-100CRCT-ND
R63, R64: 1K; R_0805_2012Metric; DigiKey RC0805FR-071KL
X5, X7: 87833-1032; DS1014-10RF1B; DigiKey WM8615-ND
X6, X8: DS1023-2*14S21; TSW-114-07-F-D; DigiKey SAM1183-14-ND
ZD1, ZD2: SMAJ16A; DO214AC-2; DigiKey SMAJ16A-FDICT-ND

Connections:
+3V3_ISO: C91.2, IC22.1 (EN), IC22.4 (EN), IC22.10 (EN), IC22.13 (EN), IC22.14 (V+), Q11.2 (S), X6.13; also elsewhere on the board
+5V_ISO: IC23.12 (VL), X6.16; also elsewhere on the board
+15V_ISO: IC23.13 (V+), Q6.E, R54.1, X6.20; also elsewhere on the board
-5V_ISO: X6.15; also elsewhere on the board
-15V_ISO: IC23.4 (V-), Q7.E, R55.1, X6.19; also elsewhere on the board
-VSENSE: IC23.2 (D), IC23.7 (D); also elsewhere on the board
/ADIB, PWM, AFE connectors/AFE1N: IC23.3 (S), X5.3, X6.25
/ADIB, PWM, AFE connectors/AFE1P: R63.1, X5.4, X6.26
/ADIB, PWM, AFE connectors/AFE2N: IC23.6 (S), X6.23, X7.3
/ADIB, PWM, AFE connectors/AFE2P: R64.1, X6.24, X7.4
ADC_CLK/SDA1: X6.4; also elsewhere on the board
ADC_START/SCL1: X6.10; also elsewhere on the board
ADIB1_ID0: X5.7; also elsewhere on the board
ADIB1_ID1: X5.9; also elsewhere on the board
ADIB1_ID2: X5.8; also elsewhere on the board
ADIB1_SW: IC23.1 (IN), IC23.16 (IN); also elsewhere on the board
ADIB2_ID0: X7.7; also elsewhere on the board
ADIB2_ID1: X7.9; also elsewhere on the board
ADIB2_ID2: X7.8; also elsewhere on the board
ADIB2_SW: IC23.8 (IN), IC23.9 (IN); also elsewhere on the board
AFE_CLK: X6.14; also elsewhere on the board
AFE_ID0: X8.1; also elsewhere on the board
AFE_ID1: X8.2; also elsewhere on the board
BIAS_EN: R56.1; also elsewhere on the board
CLAMP: D23.2 (C2), D24.2 (C2); also elsewhere on the board
DAC_OUT#1: IC23.15 (D); also elsewhere on the board
DAC_OUT#2: IC23.10 (D); also elsewhere on the board
GND: C91.1, D23.1 (A1), D24.1 (A1), IC22.7 (V-), IC23.5 (GND), Q8.E, X5.1, X5.2, X5.5, X5.6, X5.10, X6.1, X6.2, X6.11, X6.12, X6.21, X6.22, X6.27, X6.28, X7.1, X7.2, X7.5, X7.6, X7.10, X8.27, X8.28, ZD1.C, ZD2.A; also elsewhere on the board
ISEL10_R#3: X8.21; also elsewhere on the board
ISEL10_R#4: X8.22; also elsewhere on the board
ISEL10_S#3: X8.19; also elsewhere on the board
ISEL10_S#4: X8.20; also elsewhere on the board
ISEL#1: X8.3; also elsewhere on the board
ISEL#2: X8.4; also elsewhere on the board
ISEL_LOW#3: X8.23; also elsewhere on the board
ISEL_LOW#4: X8.24; also elsewhere on the board
ISEL_MID#3: X8.25; also elsewhere on the board
ISEL_MID#4: X8.26; also elsewhere on the board
ISEL_R#3: X8.17; also elsewhere on the board
ISEL_R#4: X8.18; also elsewhere on the board
ISEL_S#3: X8.15; also elsewhere on the board
ISEL_S#4: X8.16; also elsewhere on the board
MIO_MISO: X6.8; also elsewhere on the board
MIO_MOSI: X6.3; also elsewhere on the board
MIO_SCK: X6.6; also elsewhere on the board
unnamed: D23.3 (C1A2), IC22.3 (O), IC22.6 (O), R61.2
unnamed: D24.3 (C1A2), IC22.8 (O), IC22.11 (O), R62.2
unnamed: IC23.14 (S), R63.2
unnamed: IC23.11 (S), R64.2
unnamed: JP2.1, R61.1
unnamed: D25.C, JP2.3, ZD1.A
unnamed: JP3.1, R62.1
unnamed: D26.A, JP3.3, ZD2.C
unnamed: Q8.B, R56.2
unnamed: D25.A, Q9.3 (D)
unnamed: Q6.C, Q9.1 (G), R57.2, R59.1
unnamed: Q6.B, Q9.2 (S), R54.2, R57.1
unnamed: D26.C, Q10.3 (D)
unnamed: Q7.C, Q10.1 (G), R58.1, R60.2
unnamed: Q7.B, Q10.2 (S), R55.2, R58.2
unnamed: Q11.3 (D), R60.1
unnamed: Q8.C, Q11.1 (G), R59.2
PWM#1/SCK: IC22.2 (I), IC22.5 (I); also elsewhere on the board
PWM#2/MOSI: IC22.9 (I), IC22.12 (I); also elsewhere on the board
PWM_OUT#1: JP2.2; also elsewhere on the board
PWM_OUT#2: JP3.2; also elsewhere on the board
USEL1#1: X8.5; also elsewhere on the board
USEL1#2/SDA2: X8.6; also elsewhere on the board
USEL1#3: X8.11; also elsewhere on the board
USEL1#4: X8.12; also elsewhere on the board
USEL20#1: X8.7; also elsewhere on the board
USEL20#2/SCL2: X8.8; also elsewhere on the board
USEL20#3: X8.13; also elsewhere on the board
USEL20#4: X8.14; also elsewhere on the board
USEL100#1: X8.9; also elsewhere on the board
USEL100#2: X8.10; also elsewhere on the board
~ADC_CS: X6.5; also elsewhere on the board
~ADC_DRDY: X6.7; also elsewhere on the board
~RESET: X6.9; also elsewhere on the board

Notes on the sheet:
8 ADC_START / I2C_SDA1
~{CS} 5
28-pin AFE socket (upper)
22 ISEL10_R#4
ISEL#1 3
USEL100#1 9
N.C. 17
12 USEL1#4
ADIB2N 23
ISEL_S#3 15
4 ADC CLK SEL / I2C_SCL1
28 Gnd
22 Gnd
6 SPI_CLK
Gnd 11
8 USEL20#2 / I2C_SCL2
24 ISEL_LOW#4
AFE_ID0 1
Gnd 1
26 ADIB1P
AFE connectors
~{RESET} 9
12 Gnd
ISEL_MID#3 25
+5V 15
18 ISEL_R#4
Gnd 27
Licensed under the TAPR Open Hardware License (www.tapr.org/OHL) More info at http://www.envox.eu/eez-bb3 Repository: https://github.com/eez-open
Max. -10 mA
24 ADIB2P
28-pin AFE socket (lower)
4 ISEL#2
2 Gnd
6 USEL1#2 / I2C_SDA2
Max. +10 mA
+3V3 13
10 USEL100#2
26 ISEL_MID#4
Sensor bias outputs
18 N.C.

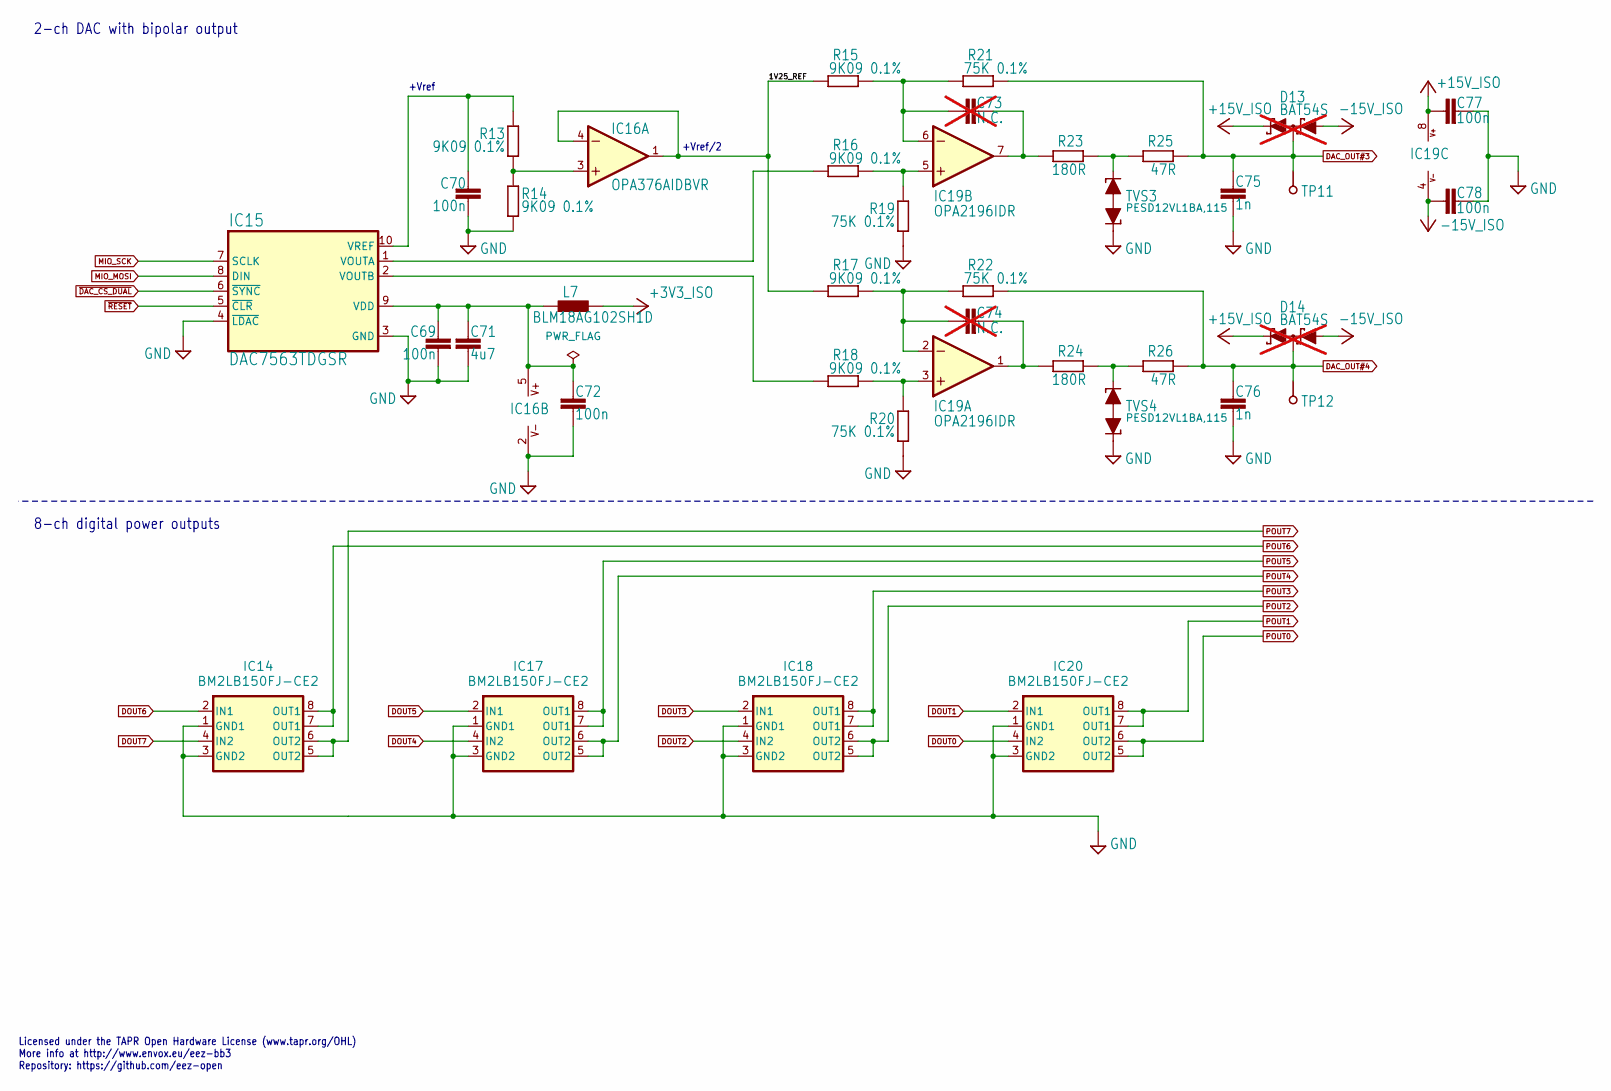
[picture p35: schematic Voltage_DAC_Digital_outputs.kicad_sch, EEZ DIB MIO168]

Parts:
C69, C70, C72, C77, C78: 100n; C_0603_1608Metric; DigiKey 1276-1005-2-ND
C71: 4u7; C_0805_2012Metric; DigiKey 490-14466-1-ND
C73, C74: N.C.; C_0805_2012Metric; not fitted
C75, C76: 1n; C_0805_2012Metric; DigiKey 732-7858-1-ND
D13, D14: BAT54S; SOT23-3; DigiKey 497-2522-1-ND; not fitted
IC14, IC17, IC18, IC20: BM2LB150FJ-CE2; SOIC127P600X173-8N; DigiKey BM2LB150FJ-CE2TR-ND
IC15: DAC7563TDGSR; DGS10; DigiKey 296-43287-1-ND
IC16: OPA376AIDBVR; SOT23-5L_STM; DigiKey 296-39130-2-ND
IC19: OPA2196IDR; SOIC127P600X173-8N; DigiKey 296-1282-1-ND
L7: BLM18AG102SH1D; BEAD0603; DigiKey 490-7809-1-ND
R13, R14, R15, R16, R17, R18: 9K09 0.1%; R_0805_2012Metric; DigiKey P9.09KDACT-ND
R19, R20, R21, R22: 75K 0.1%; R_0805_2012Metric; DigiKey P75KDACT-ND
R23, R24: 180R; R_0805_2012Metric; DigiKey A126343CT-ND
R25, R26: 47R; R_0805_2012Metric; DigiKey P47.0CCT-ND
TP11, TP12: PCB_TEST_TABSHIELD; Testhole 24_50mils
TVS3, TVS4: PESD12VL1BA,115; SOD-323_PESD; DigiKey 1727-3808-1-ND

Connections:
+3V3_ISO: L7.2; also elsewhere on the board
+15V_ISO: C77.1, D13.2 (C2), D14.2 (C2), IC19.8 (V+); also elsewhere on the board
-15V_ISO: C78.1, D13.1 (A1), D14.1 (A1), IC19.4 (V-); also elsewhere on the board
/Voltage DAC, Digital outputs/1V25_REF: IC16.1 (OUT), IC16.4 (-IN), R15.2, R17.2
DAC_OUT#3: C75.1, D13.3 (C1A2), R21.1, R25.2, TP11.1; also elsewhere on the board
DAC_OUT#4: C76.1, D14.3 (C1A2), R22.1, R26.2, TP12.1; also elsewhere on the board
DOUT0: IC20.4 (IN2); also elsewhere on the board
DOUT1: IC20.2 (IN1); also elsewhere on the board
DOUT2: IC18.4 (IN2); also elsewhere on the board
DOUT3: IC18.2 (IN1); also elsewhere on the board
DOUT4: IC17.4 (IN2); also elsewhere on the board
DOUT5: IC17.2 (IN1); also elsewhere on the board
DOUT6: IC14.2 (IN1); also elsewhere on the board
DOUT7: IC14.4 (IN2); also elsewhere on the board
GND: C69.2, C70.1, C71.1, C72.2, C75.2, C76.2, C77.2, C78.2, IC14.1 (GND1), IC14.3 (GND2), IC15.3 (GND), IC15.4 (~LDAC), IC16.2 (V-), IC17.1 (GND1), IC17.3 (GND2), IC18.1 (GND1), IC18.3 (GND2), IC20.1 (GND1), IC20.3 (GND2), R14.2, R19.2, R20.2, TVS3.C1 (1), TVS4.C1 (1); also elsewhere on the board
MIO_MOSI: IC15.8 (DIN); also elsewhere on the board
MIO_SCK: IC15.7 (SCLK); also elsewhere on the board
unnamed: C69.1, C71.2, C72.1, IC15.9 (VDD), IC16.5 (V+), L7.1
unnamed: IC15.1 (VOUTA), R16.2
unnamed: IC15.2 (VOUTB), R18.2
unnamed: C70.2, IC15.10 (VREF), R13.1
unnamed: IC16.3 (+IN), R13.2, R14.1
unnamed: IC19.3 (+IN), R18.1, R20.1
unnamed: C74.1, IC19.2 (-IN), R17.1, R22.2
unnamed: C74.2, IC19.1 (OUT), R24.1
unnamed: IC19.5 (+IN), R16.1, R19.1
unnamed: C73.1, IC19.6 (-IN), R15.1, R21.2
unnamed: C73.2, IC19.7 (OUT), R23.1
unnamed: R23.2, R25.1, TVS3.C2 (2)
unnamed: R24.2, R26.1, TVS4.C2 (2)
POUT0: IC20.5 (OUT2), IC20.6 (OUT2); also elsewhere on the board
POUT1: IC20.7 (OUT1), IC20.8 (OUT1); also elsewhere on the board
POUT2: IC18.5 (OUT2), IC18.6 (OUT2); also elsewhere on the board
POUT3: IC18.7 (OUT1), IC18.8 (OUT1); also elsewhere on the board
POUT4: IC17.5 (OUT2), IC17.6 (OUT2); also elsewhere on the board
POUT5: IC17.7 (OUT1), IC17.8 (OUT1); also elsewhere on the board
POUT6: IC14.7 (OUT1), IC14.8 (OUT1); also elsewhere on the board
POUT7: IC14.5 (OUT2), IC14.6 (OUT2); also elsewhere on the board
~DAC_CS_DUAL: IC15.6 (~SYNC); also elsewhere on the board
~RESET: IC15.5 (~CLR); also elsewhere on the board

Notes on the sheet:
+Vref
+Vref/2
8-ch digital power outputs
2-ch DAC with bipolar output
Licensed under the TAPR Open Hardware License (www.tapr.org/OHL) More info at http://www.envox.eu/eez-bb3 Repository: https://github.com/eez-open

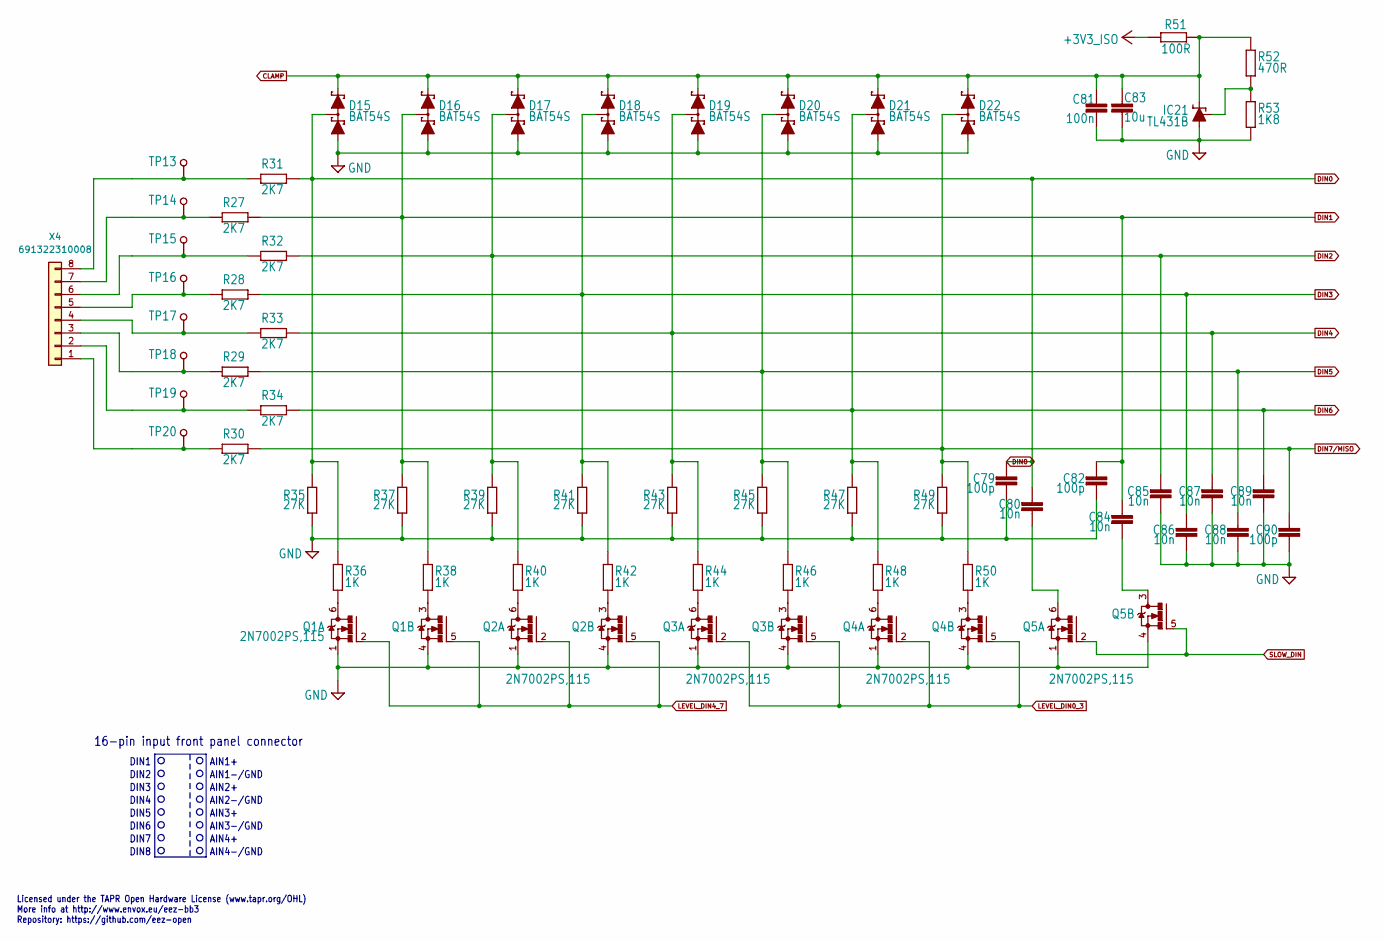
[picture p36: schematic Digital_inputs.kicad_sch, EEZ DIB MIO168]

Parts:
C79, C82, C90: 100p; C_0805_2012Metric; DigiKey 399-15000-1-ND
C80, C84, C85, C86, C87, C88, C89: 10n; C_0805_2012Metric; DigiKey 490-7194-1-ND
C81: 100n; C_0603_1608Metric; DigiKey 1276-1005-2-ND
C83: 10u; C_1206_3216Metric; DigiKey 1276-2872-1-ND
D15, D16, D17, D18, D19, D20, D21, D22: BAT54S; SOT23-3; DigiKey 497-2522-1-ND
IC21: TL431B; SOT103P240X110-3N; DigiKey 296-17332-1-ND
Q1, Q2, Q3, Q4, Q5: 2N7002PS,115; SC88; DigiKey 1727-4791-2-ND
R27, R28, R29, R30, R31, R32, R33, R34: 2K7; R_1206_3216Metric; DigiKey 311-2.70KFRCT-ND
R35, R37, R39, R41, R43, R45, R47, R49: 27K; R_0805_2012Metric; DigiKey A126356CT-ND
R36, R38, R40, R42, R44, R46, R48, R50: 1K; R_0805_2012Metric; DigiKey RC0805FR-071KL
R51: 100R; R_0805_2012Metric; DigiKey 311-100CRCT-ND
R52: 470R; R_0805_2012Metric; DigiKey 311-470CRCT-ND
R53: 1K8; R_0805_2012Metric; DigiKey A129752CT-ND
TP13, TP14, TP15, TP16, TP17, TP18, TP19, TP20: PCB_TEST_TABSHIELD; Testhole 24_50mils
X4: 691322310008; DigiKey 732-2093-ND

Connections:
+3V3_ISO: R51.1; also elsewhere on the board
CLAMP: C81.1, C83.1, D15.2 (C2), D16.2 (C2), D17.2 (C2), D18.2 (C2), D19.2 (C2), D20.2 (C2), D21.2 (C2), D22.2 (C2), IC21.1 (C), R51.2, R52.1; also elsewhere on the board
DIN0: C79.1, C80.1, D15.3 (C1A2), R31.2, R35.2, R36.1; also elsewhere on the board
DIN1: C82.1, C84.1, D16.3 (C1A2), R27.2, R37.2, R38.1; also elsewhere on the board
DIN2: C85.1, D17.3 (C1A2), R32.2, R39.2, R40.1; also elsewhere on the board
DIN3: C86.1, D18.3 (C1A2), R28.2, R41.2, R42.1; also elsewhere on the board
DIN4: C87.1, D19.3 (C1A2), R33.2, R43.2, R44.1; also elsewhere on the board
DIN5: C88.1, D20.3 (C1A2), R29.2, R45.2, R46.1; also elsewhere on the board
DIN6: C89.1, D21.3 (C1A2), R34.2, R47.2, R48.1; also elsewhere on the board
DIN7/MISO: C90.1, D22.3 (C1A2), R30.2, R49.2, R50.1; also elsewhere on the board
GND: C79.2, C81.2, C82.2, C83.2, C85.2, C86.2, C87.2, C88.2, C89.2, C90.2, D15.1 (A1), D16.1 (A1), D17.1 (A1), D18.1 (A1), D19.1 (A1), D20.1 (A1), D21.1 (A1), D22.1 (A1), IC21.3 (A), Q1.1 (S), Q1.4 (S), Q2.1 (S), Q2.4 (S), Q3.1 (S), Q3.4 (S), Q4.1 (S), Q4.4 (S), Q5.1 (S), Q5.4 (S), R35.1, R37.1, R39.1, R41.1, R43.1, R45.1, R47.1, R49.1, R53.2; also elsewhere on the board
LEVEL_DIN0_3: Q3.2 (G), Q3.5 (G), Q4.2 (G), Q4.5 (G); also elsewhere on the board
LEVEL_DIN4_7: Q1.2 (G), Q1.5 (G), Q2.2 (G), Q2.5 (G); also elsewhere on the board
unnamed: IC21.2 (R), R52.2, R53.1
unnamed: Q1.6 (D), R36.2
unnamed: Q1.3 (D), R38.2
unnamed: Q2.6 (D), R40.2
unnamed: Q2.3 (D), R42.2
unnamed: Q3.6 (D), R44.2
unnamed: Q3.3 (D), R46.2
unnamed: Q4.6 (D), R48.2
unnamed: Q4.3 (D), R50.2
unnamed: C80.2, Q5.6 (D)
unnamed: C84.2, Q5.3 (D)
unnamed: R31.1, TP13.1, X4.8
unnamed: R27.1, TP14.1, X4.7
unnamed: R32.1, TP15.1, X4.6
unnamed: R28.1, TP16.1, X4.5
unnamed: R33.1, TP17.1, X4.4
unnamed: R29.1, TP18.1, X4.3
unnamed: R34.1, TP19.1, X4.2
unnamed: R30.1, TP20.1, X4.1
SLOW_DIN: Q5.2 (G), Q5.5 (G); also elsewhere on the board

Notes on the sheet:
DIN4
Licensed under the TAPR Open Hardware License (www.tapr.org/OHL) More info at http://www.envox.eu/eez-bb3 Repository: https://github.com/eez-open
AIN1-/GND
DIN6
AIN3+
AIN3-/GND
DIN2
DIN3
AIN1+
AIN4-/GND
DIN7
16-pin input front panel connector
AIN2+
AIN4+
DIN8
DIN5
AIN2-/GND
DIN1

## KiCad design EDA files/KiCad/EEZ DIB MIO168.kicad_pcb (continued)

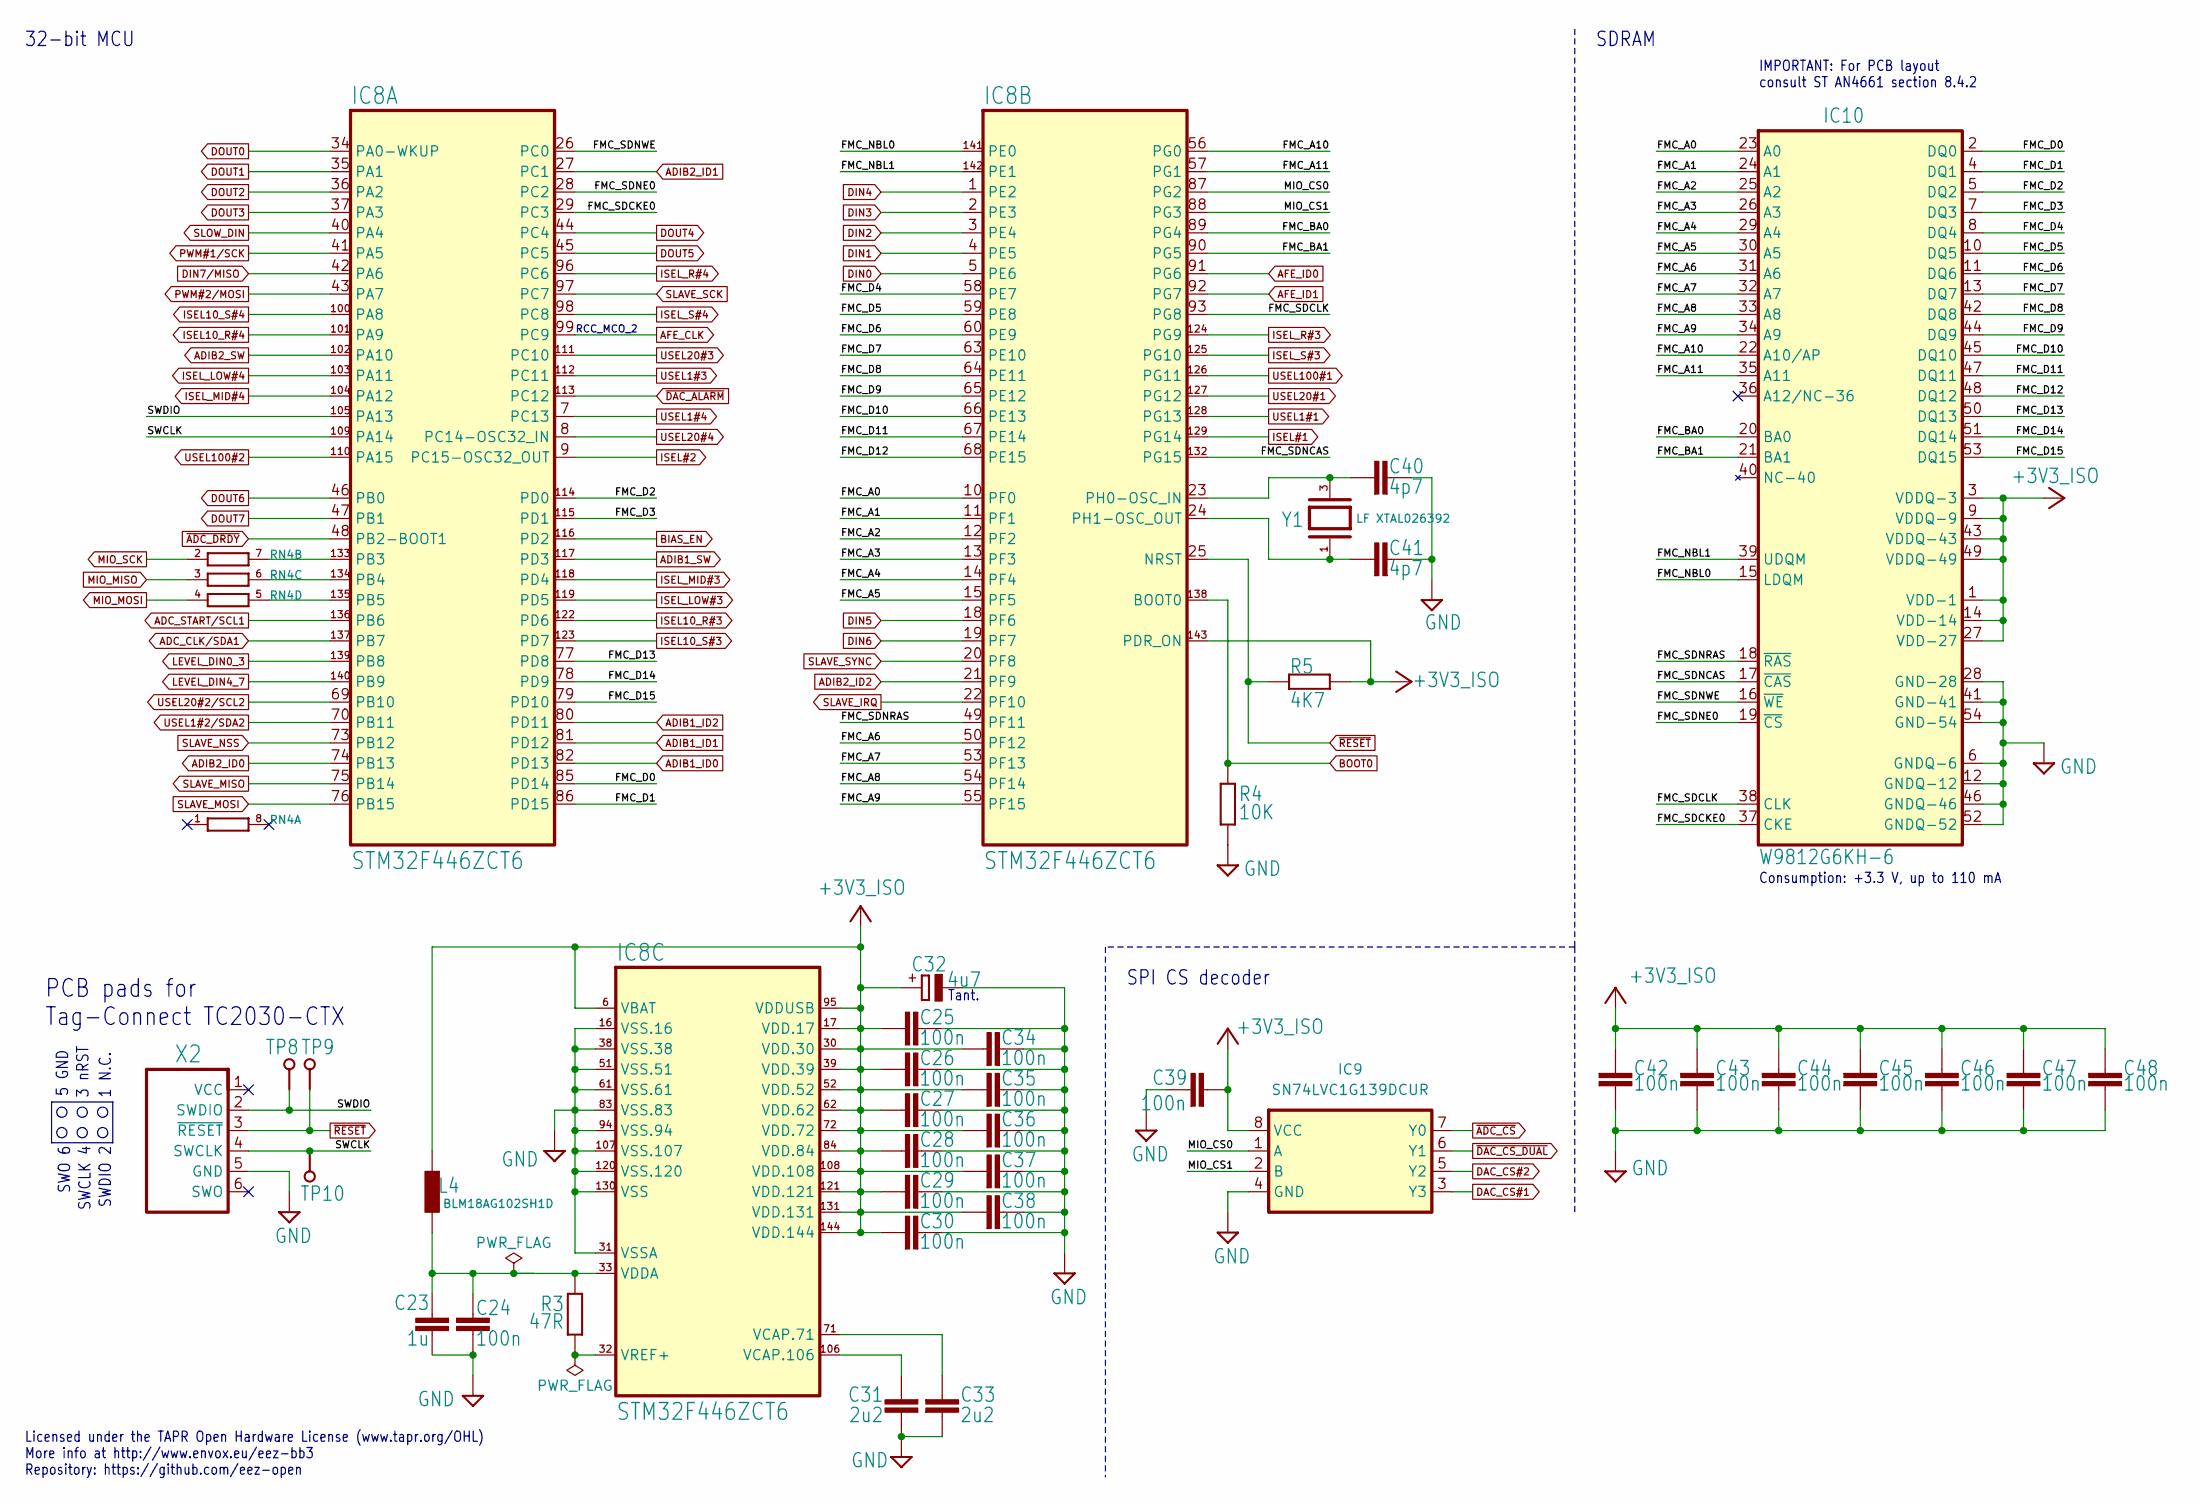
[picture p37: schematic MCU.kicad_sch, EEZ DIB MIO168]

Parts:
C23: 1u; C_0805_2012Metric; DigiKey 490-10494-2-ND
C24, C25, C26, C27, C28, C29, C30, C34, C35, C36, C37, C38, C39, C42, C43, C44, C45, C46, C47, C48: 100n; C_0603_1608Metric; DigiKey 1276-1005-2-ND
C31, C33: 2u2; C_0805_2012Metric; DigiKey 1276-2954-1-ND
C32: 4u7; EC1206; DigiKey 399-9717-1-ND
C40, C41: 4p7; C_0603_1608Metric; DigiKey 311-1740-1-ND
IC8: STM32F446ZCT6; LQFP-144_20X20MM; DigiKey 497-17473-ND
IC9: SN74LVC1G139DCUR; DCU8; DigiKey 296-18203-2-ND
IC10: W9812G6KH-6; TSOPII-54; DigiKey W9812G6KH-6-ND
L4: BLM18AG102SH1D; BEAD0603; DigiKey 490-7809-1-ND
R3: 47R; R_0805_2012Metric; DigiKey P47.0CCT-ND
R4: 10K; R_0805_2012Metric; DigiKey CRGH0603F10K
R5: 4K7; R_0805_2012Metric; DigiKey 311-4.70KCRCT-ND
RN4: DR1206-33R-4/8; CAY16; DigiKey CAY16-330J4LFCT-ND
TP8, TP9, TP10: PCB_TEST_TABSHIELD; Testhole 24_50mils
X2: TC2030
Y1: LF XTAL026392; 12SMX(B); DigiKey 1923-1009-ND

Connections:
+3V3_ISO: C25.1, C26.1, C27.1, C28.1, C29.1, C30.1, C32.+, C34.1, C35.1, C36.1, C37.1, C38.1, C39.1, C42.1, C43.1, C44.1, C45.1, C46.1, C47.1, C48.1, IC8.6 (VBAT), IC8.17 (VDD.17), IC8.30 (VDD.30), IC8.39 (VDD.39), IC8.52 (VDD.52), IC8.62 (VDD.62), IC8.72 (VDD.72), IC8.84 (VDD.84), IC8.95 (VDDUSB), IC8.108 (VDD.108), IC8.121 (VDD.121), IC8.131 (VDD.131), IC8.143 (PDR_ON), IC8.144 (VDD.144), IC9.8 (VCC), IC10.1 (VDD-1), IC10.3 (VDDQ-3), IC10.9 (VDDQ-9), IC10.14 (VDD-14), IC10.27 (VDD-27), IC10.43 (VDDQ-43), IC10.49 (VDDQ-49), L4.1, R5.1; also elsewhere on the board
/MCU/FMC_A0: IC8.10 (PF0), IC10.23 (A0)
/MCU/FMC_A1: IC8.11 (PF1), IC10.24 (A1)
/MCU/FMC_A2: IC8.12 (PF2), IC10.25 (A2)
/MCU/FMC_A3: IC8.13 (PF3), IC10.26 (A3)
/MCU/FMC_A4: IC8.14 (PF4), IC10.29 (A4)
/MCU/FMC_A5: IC8.15 (PF5), IC10.30 (A5)
/MCU/FMC_A6: IC8.50 (PF12), IC10.31 (A6)
/MCU/FMC_A7: IC8.53 (PF13), IC10.32 (A7)
/MCU/FMC_A8: IC8.54 (PF14), IC10.33 (A8)
/MCU/FMC_A9: IC8.55 (PF15), IC10.34 (A9)
/MCU/FMC_A10: IC8.56 (PG0), IC10.22 (A10/AP)
/MCU/FMC_A11: IC8.57 (PG1), IC10.35 (A11)
/MCU/FMC_BA0: IC8.89 (PG4), IC10.20 (BA0)
/MCU/FMC_BA1: IC8.90 (PG5), IC10.21 (BA1)
/MCU/FMC_D0: IC8.85 (PD14), IC10.2 (DQ0)
/MCU/FMC_D1: IC8.86 (PD15), IC10.4 (DQ1)
/MCU/FMC_D2: IC8.114 (PD0), IC10.5 (DQ2)
/MCU/FMC_D3: IC8.115 (PD1), IC10.7 (DQ3)
/MCU/FMC_D4: IC8.58 (PE7), IC10.8 (DQ4)
/MCU/FMC_D5: IC8.59 (PE8), IC10.10 (DQ5)
/MCU/FMC_D6: IC8.60 (PE9), IC10.11 (DQ6)
/MCU/FMC_D7: IC8.63 (PE10), IC10.13 (DQ7)
/MCU/FMC_D8: IC8.64 (PE11), IC10.42 (DQ8)
/MCU/FMC_D9: IC8.65 (PE12), IC10.44 (DQ9)
/MCU/FMC_D10: IC8.66 (PE13), IC10.45 (DQ10)
/MCU/FMC_D11: IC8.67 (PE14), IC10.47 (DQ11)
/MCU/FMC_D12: IC8.68 (PE15), IC10.48 (DQ12)
/MCU/FMC_D13: IC8.77 (PD8), IC10.50 (DQ13)
/MCU/FMC_D14: IC8.78 (PD9), IC10.51 (DQ14)
/MCU/FMC_D15: IC8.79 (PD10), IC10.53 (DQ15)
/MCU/FMC_NBL0: IC8.141 (PE0), IC10.15 (LDQM)
/MCU/FMC_NBL1: IC8.142 (PE1), IC10.39 (UDQM)
/MCU/FMC_SDCKE0: IC8.29 (PC3), IC10.37 (CKE)
/MCU/FMC_SDCLK: IC8.93 (PG8), IC10.38 (CLK)
/MCU/FMC_SDNCAS: IC8.132 (PG15), IC10.17 (~CAS)
/MCU/FMC_SDNE0: IC8.28 (PC2), IC10.19 (~CS)
/MCU/FMC_SDNRAS: IC8.49 (PF11), IC10.18 (~RAS)
/MCU/FMC_SDNWE: IC8.26 (PC0), IC10.16 (~WE)
/MCU/MIO_CS0: IC8.87 (PG2), IC9.1 (A)
/MCU/MIO_CS1: IC8.88 (PG3), IC9.2 (B)
/MCU/SWCLK: IC8.109 (PA14), TP10.1, X2.4 (SWCLK)
/MCU/SWDIO: IC8.105 (PA13), TP8.1, X2.2 (SWDIO)
ADC_CLK/SDA1: IC8.137 (PB7); also elsewhere on the board
ADC_START/SCL1: IC8.136 (PB6); also elsewhere on the board
ADIB1_ID0: IC8.82 (PD13); also elsewhere on the board
ADIB1_ID1: IC8.81 (PD12); also elsewhere on the board
ADIB1_ID2: IC8.80 (PD11); also elsewhere on the board
ADIB1_SW: IC8.117 (PD3); also elsewhere on the board
ADIB2_ID0: IC8.74 (PB13); also elsewhere on the board
ADIB2_ID1: IC8.27 (PC1); also elsewhere on the board
ADIB2_ID2: IC8.21 (PF9); also elsewhere on the board
ADIB2_SW: IC8.102 (PA10); also elsewhere on the board
AFE_CLK: IC8.99 (PC9); also elsewhere on the board
AFE_ID0: IC8.91 (PG6); also elsewhere on the board
AFE_ID1: IC8.92 (PG7); also elsewhere on the board
BIAS_EN: IC8.116 (PD2); also elsewhere on the board
BOOT0: IC8.138 (BOOT0), R4.2; also elsewhere on the board
DAC_CS#1: IC9.3 (Y3); also elsewhere on the board
DAC_CS#2: IC9.5 (Y2); also elsewhere on the board
DIN0: IC8.5 (PE6); also elsewhere on the board
DIN1: IC8.4 (PE5); also elsewhere on the board
DIN2: IC8.3 (PE4); also elsewhere on the board
DIN3: IC8.2 (PE3); also elsewhere on the board
DIN4: IC8.1 (PE2); also elsewhere on the board
DIN5: IC8.18 (PF6); also elsewhere on the board
DIN6: IC8.19 (PF7); also elsewhere on the board
DIN7/MISO: IC8.42 (PA6); also elsewhere on the board
DOUT0: IC8.34 (PA0-WKUP); also elsewhere on the board
DOUT1: IC8.35 (PA1); also elsewhere on the board
DOUT2: IC8.36 (PA2); also elsewhere on the board
DOUT3: IC8.37 (PA3); also elsewhere on the board
DOUT4: IC8.44 (PC4); also elsewhere on the board
DOUT5: IC8.45 (PC5); also elsewhere on the board
DOUT6: IC8.46 (PB0); also elsewhere on the board
DOUT7: IC8.47 (PB1); also elsewhere on the board
GND: C23.2, C24.2, C25.2, C26.2, C27.2, C28.2, C29.2, C30.2, C31.1, C32.-, C33.1, C34.2, C35.2, C36.2, C37.2, C38.2, C39.2, C40.1, C41.1, C42.2, C43.2, C44.2, C45.2, C46.2, C47.2, C48.2, IC8.16 (VSS.16), IC8.31 (VSSA), IC8.38 (VSS.38), IC8.51 (VSS.51), IC8.61 (VSS.61), IC8.83 (VSS.83), IC8.94 (VSS.94), IC8.107 (VSS.107), IC8.120 (VSS.120), IC8.130 (VSS), IC9.4 (GND), IC10.6 (GNDQ-6), IC10.12 (GNDQ-12), IC10.28 (GND-28), IC10.41 (GND-41), IC10.46 (GNDQ-46), IC10.52 (GNDQ-52), IC10.54 (GND-54), R4.1, X2.5 (GND); also elsewhere on the board
ISEL10_R#3: IC8.122 (PD6); also elsewhere on the board
ISEL10_R#4: IC8.101 (PA9); also elsewhere on the board
ISEL10_S#3: IC8.123 (PD7); also elsewhere on the board
ISEL10_S#4: IC8.100 (PA8); also elsewhere on the board
ISEL#1: IC8.129 (PG14); also elsewhere on the board
ISEL#2: IC8.9 (PC15-OSC32_OUT); also elsewhere on the board
ISEL_LOW#3: IC8.119 (PD5); also elsewhere on the board
ISEL_LOW#4: IC8.103 (PA11); also elsewhere on the board
ISEL_MID#3: IC8.118 (PD4); also elsewhere on the board
ISEL_MID#4: IC8.104 (PA12); also elsewhere on the board
ISEL_R#3: IC8.124 (PG9); also elsewhere on the board
ISEL_R#4: IC8.96 (PC6); also elsewhere on the board
ISEL_S#3: IC8.125 (PG10); also elsewhere on the board
ISEL_S#4: IC8.98 (PC8); also elsewhere on the board
LEVEL_DIN0_3: IC8.139 (PB8); also elsewhere on the board
LEVEL_DIN4_7: IC8.140 (PB9); also elsewhere on the board
MIO_MISO: RN4.3 (1); also elsewhere on the board
MIO_MOSI: RN4.4 (1); also elsewhere on the board
MIO_SCK: RN4.2 (1); also elsewhere on the board
unnamed: IC8.133 (PB3), RN4.7 (2)
unnamed: IC8.134 (PB4), RN4.6 (2)
unnamed: IC8.135 (PB5), RN4.5 (2)
unnamed: C40.2, IC8.23 (PH0-OSC_IN), Y1.3, Y1.4 (NC)
unnamed: C41.2, IC8.24 (PH1-OSC_OUT), Y1.1, Y1.2 (NC)
unnamed: C33.2, IC8.71 (VCAP.71)
unnamed: C31.2, IC8.106 (VCAP.106)
unnamed: C23.1, C24.1, IC8.33 (VDDA), L4.2, R3.1
unnamed: IC8.32 (VREF+), R3.2
PWM#1/SCK: IC8.41 (PA5); also elsewhere on the board
PWM#2/MOSI: IC8.43 (PA7); also elsewhere on the board
SLAVE_IRQ: IC8.22 (PF10); also elsewhere on the board
SLAVE_MISO: IC8.75 (PB14); also elsewhere on the board
SLAVE_MOSI: IC8.76 (PB15); also elsewhere on the board
SLAVE_NSS: IC8.73 (PB12); also elsewhere on the board
SLAVE_SCK: IC8.97 (PC7); also elsewhere on the board
SLAVE_SYNC: IC8.20 (PF8); also elsewhere on the board
SLOW_DIN: IC8.40 (PA4); also elsewhere on the board
USEL1#1: IC8.128 (PG13); also elsewhere on the board
USEL1#2/SDA2: IC8.70 (PB11); also elsewhere on the board
USEL1#3: IC8.112 (PC11); also elsewhere on the board
USEL1#4: IC8.7 (PC13); also elsewhere on the board
USEL20#1: IC8.127 (PG12); also elsewhere on the board
USEL20#2/SCL2: IC8.69 (PB10); also elsewhere on the board
USEL20#3: IC8.111 (PC10); also elsewhere on the board
USEL20#4: IC8.8 (PC14-OSC32_IN); also elsewhere on the board
USEL100#1: IC8.126 (PG11); also elsewhere on the board
USEL100#2: IC8.110 (PA15); also elsewhere on the board
~ADC_CS: IC9.7 (Y0); also elsewhere on the board
~ADC_DRDY: IC8.48 (PB2-BOOT1); also elsewhere on the board
~DAC_ALARM: IC8.113 (PC12); also elsewhere on the board
~DAC_CS_DUAL: IC9.6 (Y1); also elsewhere on the board
~RESET: IC8.25 (NRST), R5.2, TP9.1, X2.3 (~RESET); also elsewhere on the board

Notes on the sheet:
3 nRST
SWO 6
32-bit MCU
SWCLK 4
SWDIO 2
1 N.C.
Tant.
RCC_MCO_2
5 GND
PCB pads for Tag-Connect TC2030-CTX
Consumption: +3.3 V, up to 110 mA
SPI CS decoder
SDRAM
IMPORTANT: For PCB layout consult ST AN4661 section 8.4.2
Licensed under the TAPR Open Hardware License (www.tapr.org/OHL) More info at http://www.envox.eu/eez-bb3 Repository: https://github.com/eez-open

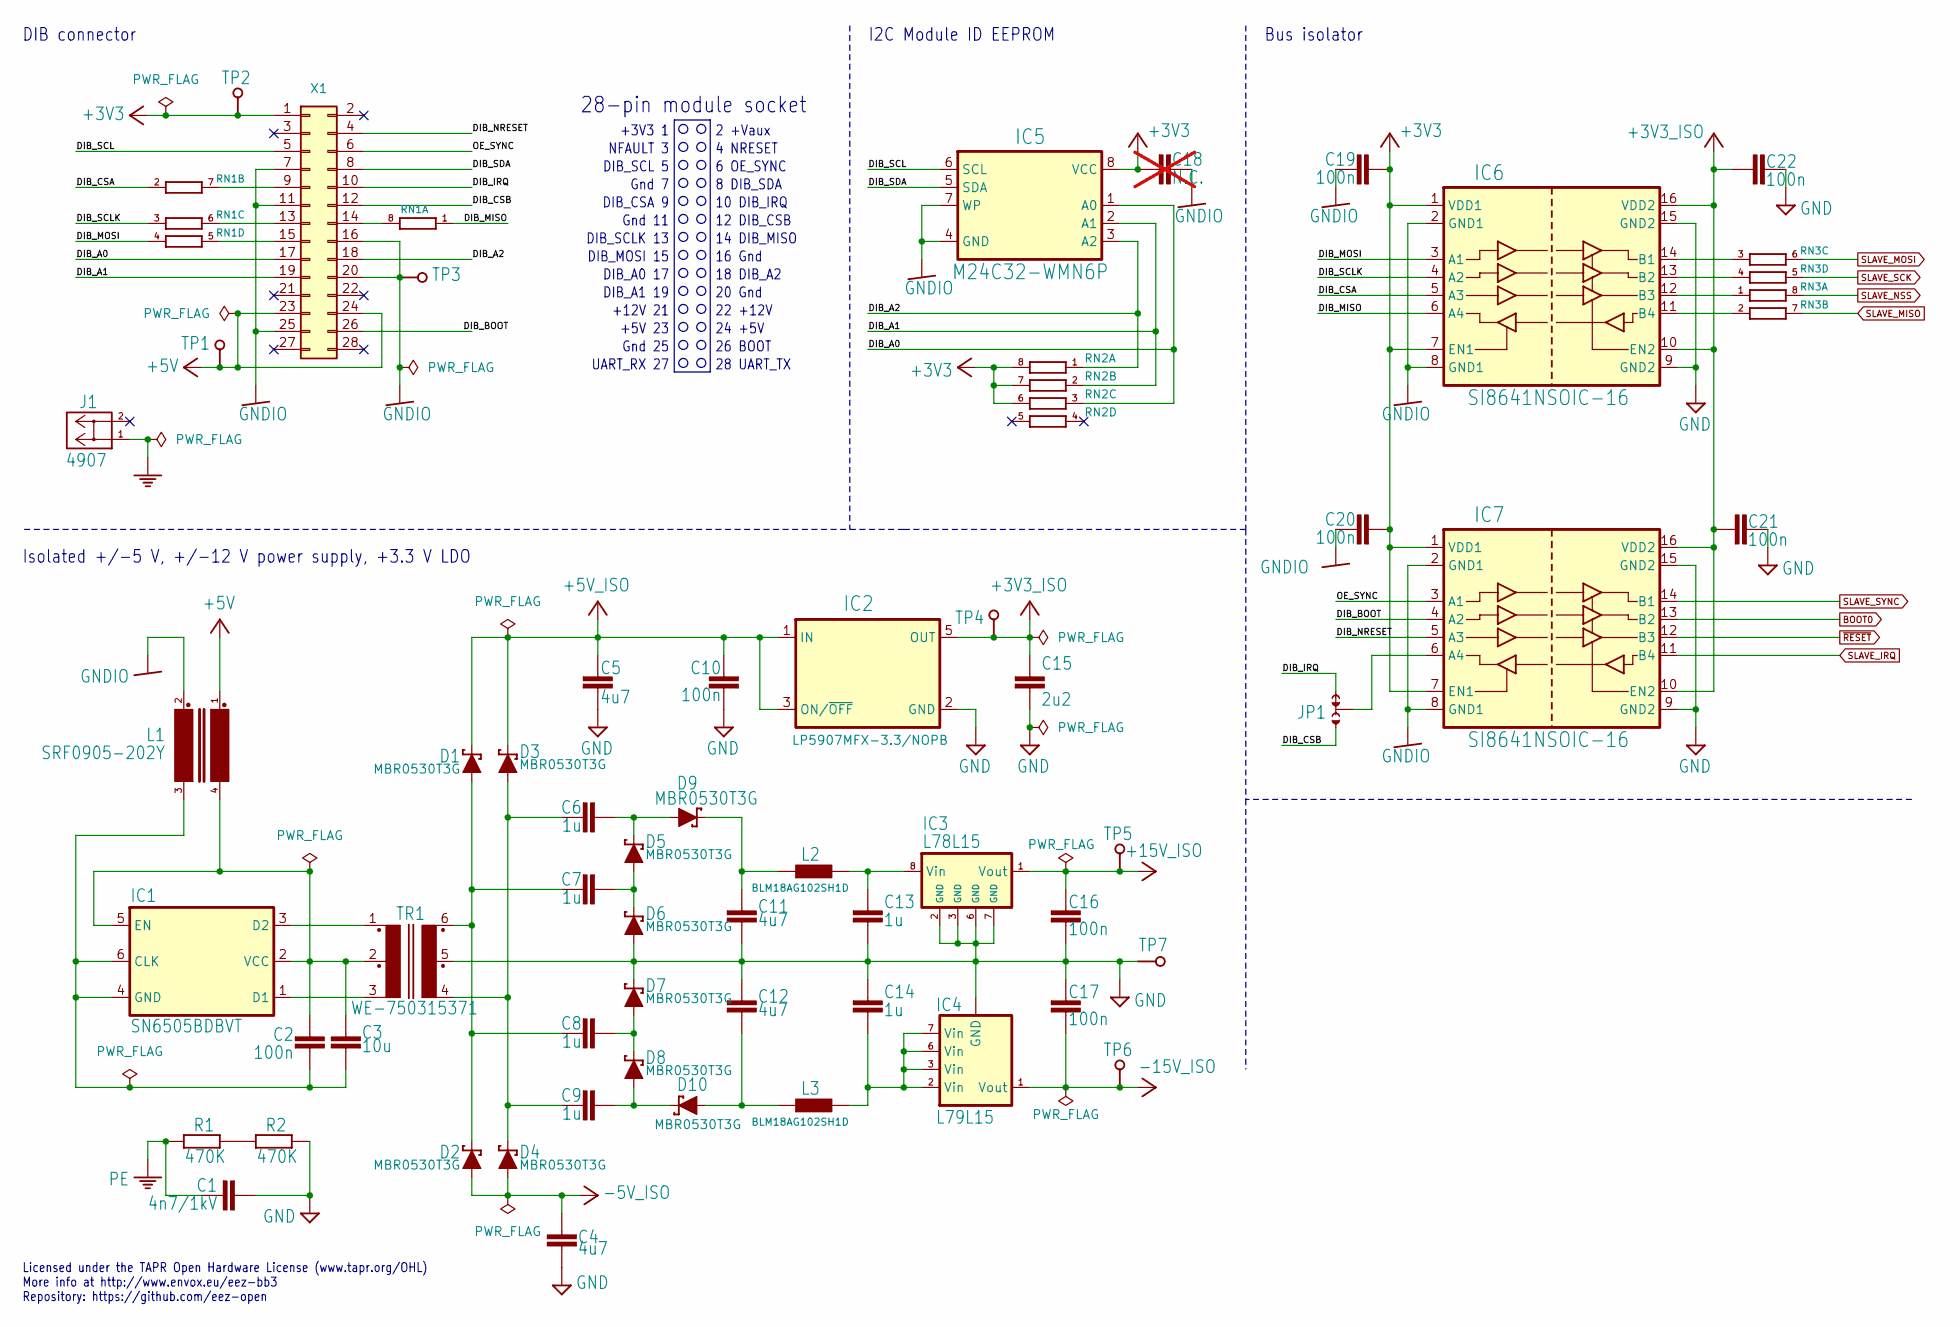
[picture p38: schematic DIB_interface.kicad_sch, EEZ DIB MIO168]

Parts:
C1: 4n7/1kV; C_1206_3216Metric; DigiKey 732-12074-2-ND
C2, C10, C16, C17, C19, C20, C21, C22: 100n; C_0603_1608Metric; DigiKey 1276-1005-2-ND
C3: 10u; C_1206_3216Metric; DigiKey 1276-2872-1-ND
C4, C5, C11, C12: 4u7; C_0805_2012Metric; DigiKey 490-14466-1-ND
C6, C7, C8, C9, C13, C14: 1u; C_0805_2012Metric; DigiKey 490-10494-2-ND
C15: 2u2; C_0805_2012Metric; DigiKey 1276-2954-1-ND
C18: N.C.; C_0603_1608Metric; not fitted
D1, D2, D3, D4, D5, D6, D7, D8, D9, D10: MBR0530T3G; SOD123; DigiKey 863-MBR0530T3G
IC1: SN6505BDBVT; DBV0006A_N; DigiKey 296-43154-2-ND
IC2: LP5907MFX-3.3/NOPB; SOT23-5L_STM; DigiKey 296-38557-2-ND
IC3: L78L15; SOIC127P600X173-8N; DigiKey MC78L15ACDR2GOSDKR-ND
IC4: L79L15; SOIC127P600X173-8N; DigiKey MC79L15ABDR2GOSDKR
IC5: M24C32-WMN6P; SOIC127P600X173-8N; DigiKey 497-8572-5-ND
IC6, IC7: SI8641NSOIC-16; SOIC127P600X265-16N; DigiKey 336-2566-ND
J1: 4907; DigiKey 36-4907-ND
JP1: JP3-CUT-0805-ROTATED; JP3 shorted
L1: SRF0905-202Y; SRF0905; DigiKey SRF0905-202YCT-ND
L2, L3: BLM18AG102SH1D; BEAD0603; DigiKey 490-7809-1-ND
R1, R2: 470K; R_0805_2012Metric; DigiKey 13-RT0805FRE07470KLDKR-ND
RN1, RN3: DR1206-33R-4/8; CAY16; DigiKey CAY16-330J4LFCT-ND
RN2: DR1206-47K-4/8; CAY16; DigiKey CAY16-330J4LFCT-ND
TP1, TP2, TP3, TP4, TP5, TP6, TP7: PCB_TEST_TABSHIELD; Testhole 24_50mils
TR1: WE-750315371; MURATA_78615; DigiKey 1297-1178-1-ND
X1: 77317-104-28LF; DigiKey S2111EC-14-ND

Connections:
+3V3: C18.2, C19.1, C20.1, IC5.8 (VCC), IC6.1 (VDD1), IC6.7 (EN1), IC7.1 (VDD1), IC7.7 (EN1), RN2.6 (2), RN2.7 (2), RN2.8 (2), TP2.1, X1.1
+3V3_ISO: C15.1, C21.2, C22.2, IC2.5 (OUT), IC6.10 (EN2), IC6.16 (VDD2), IC7.10 (EN2), IC7.16 (VDD2), TP4.1; also elsewhere on the board
+5V: L1.1, TP1.1, X1.23, X1.24
+5V_ISO: C5.2, C10.1, D1.C, D3.C, IC2.1 (IN), IC2.3 (ON/~OFF); also elsewhere on the board
+15V_ISO: C16.1, IC3.1 (Vout), TP5.1; also elsewhere on the board
-5V_ISO: C4.2, D2.A, D4.A; also elsewhere on the board
-15V_ISO: C17.2, IC4.1 (Vout), TP6.1; also elsewhere on the board
/DIB interface/DIB_A0: IC5.1 (A0), RN2.3 (1), X1.17
/DIB interface/DIB_A1: IC5.2 (A1), RN2.2 (1), X1.19
/DIB interface/DIB_A2: IC5.3 (A2), RN2.1, X1.18
/DIB interface/DIB_BOOT: IC7.4 (A2), X1.26
/DIB interface/DIB_CSA: IC6.5 (A3), RN1.2 (1)
/DIB interface/DIB_CSB: JP1.NO, X1.12
/DIB interface/DIB_IRQ: JP1.NC, X1.10
/DIB interface/DIB_MISO: IC6.6 (A4), RN1.1
/DIB interface/DIB_MOSI: IC6.3 (A1), RN1.4 (1)
/DIB interface/DIB_NRESET: IC7.5 (A3), X1.4
/DIB interface/DIB_SCL: IC5.6 (SCL), X1.5
/DIB interface/DIB_SCLK: IC6.4 (A2), RN1.3 (1)
/DIB interface/DIB_SDA: IC5.5 (SDA), X1.8
/DIB interface/OE_SYNC: IC7.3 (A1), X1.6
BOOT0: IC7.13 (B2); also elsewhere on the board
GND: C1.2, C4.1, C5.1, C10.2, C11.2, C12.1, C13.1, C14.2, C15.2, C16.2, C17.1, C21.1, C22.1, D6.A, D7.C, IC2.2 (GND), IC3.2 (GND), IC3.3 (GND), IC3.6 (GND), IC3.7 (GND), IC4.5 (GND), IC6.9 (GND2), IC6.15 (GND2), IC7.9 (GND2), IC7.15 (GND2), R2.2, TP7.1, TR1.5; also elsewhere on the board
GNDIO: C18.1, C19.2, C20.2, IC5.4 (GND), IC5.7 (WP), IC6.2 (GND1), IC6.8 (GND1), IC7.2 (GND1), IC7.8 (GND1), L1.2, TP3.1, X1.7, X1.11, X1.16, X1.20, X1.25
unnamed: C6.1, D5.C, D9.A
unnamed: C6.2, C9.2, D3.A, D4.C, TR1.4
unnamed: C7.1, D5.A, D6.C
unnamed: C7.2, C8.2, D1.A, D2.C, TR1.6
unnamed: C8.1, D7.A, D8.C
unnamed: C9.1, D8.A, D10.C
unnamed: C11.1, D9.C, L2.1
unnamed: C12.2, D10.A, L3.1
unnamed: C14.1, IC4.2 (Vin), IC4.3 (Vin), IC4.6 (Vin), IC4.7 (Vin), L3.2
unnamed: C2.2, C3.1, IC1.4 (GND), IC1.6 (CLK), L1.3
unnamed: IC1.1 (D1), TR1.3
unnamed: IC1.3 (D2), TR1.1
unnamed: C2.1, C3.2, IC1.2 (VCC), IC1.5 (EN), L1.4, TR1.2
unnamed: C13.2, IC3.8 (Vin), L2.2
unnamed: IC6.14 (B1), RN3.3 (1)
unnamed: IC6.13 (B2), RN3.4 (1)
unnamed: IC6.12 (B3), RN3.1
unnamed: IC6.11 (B4), RN3.2 (1)
unnamed: IC7.6 (A4), JP1.COM
unnamed: R1.2, R2.1
unnamed: RN1.8 (2), X1.14
unnamed: RN1.7 (2), X1.9
unnamed: RN1.6 (2), X1.13
unnamed: RN1.5 (2), X1.15
PE: C1.1, J1.1, R1.1
SLAVE_IRQ: IC7.11 (B4); also elsewhere on the board
SLAVE_MISO: RN3.7 (2); also elsewhere on the board
SLAVE_MOSI: RN3.6 (2); also elsewhere on the board
SLAVE_NSS: RN3.8 (2); also elsewhere on the board
SLAVE_SCK: RN3.5 (2); also elsewhere on the board
SLAVE_SYNC: IC7.14 (B1); also elsewhere on the board
~RESET: IC7.12 (B3); also elsewhere on the board

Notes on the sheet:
24 +5V
18 DIB_A2
28 UART_TX
DIB_A0 17
16 Gnd
DIB_A1 19
6 OE_SYNC
Licensed under the TAPR Open Hardware License (www.tapr.org/OHL) More info at http://www.envox.eu/eez-bb3 Repository: https://github.com/eez-open
Isolated +/-5 V, +/-12 V power supply, +3.3 V LDO
20 Gnd
DIB_SCLK 13
12 DIB_CSB
2 +Vaux
+5V 23
UART_RX 27
22 +12V
DIB connector
8 DIB_SDA
10 DIB_IRQ
DIB_MOSI 15
Gnd 25
DIB_CSA 9
NFAULT 3
I2C Module ID EEPROM
4 NRESET
Gnd 7
DIB_SCL 5
14 DIB_MISO
+3V3 1
Gnd 11
26 BOOT
+12V 21
Bus isolator
28-pin module socket

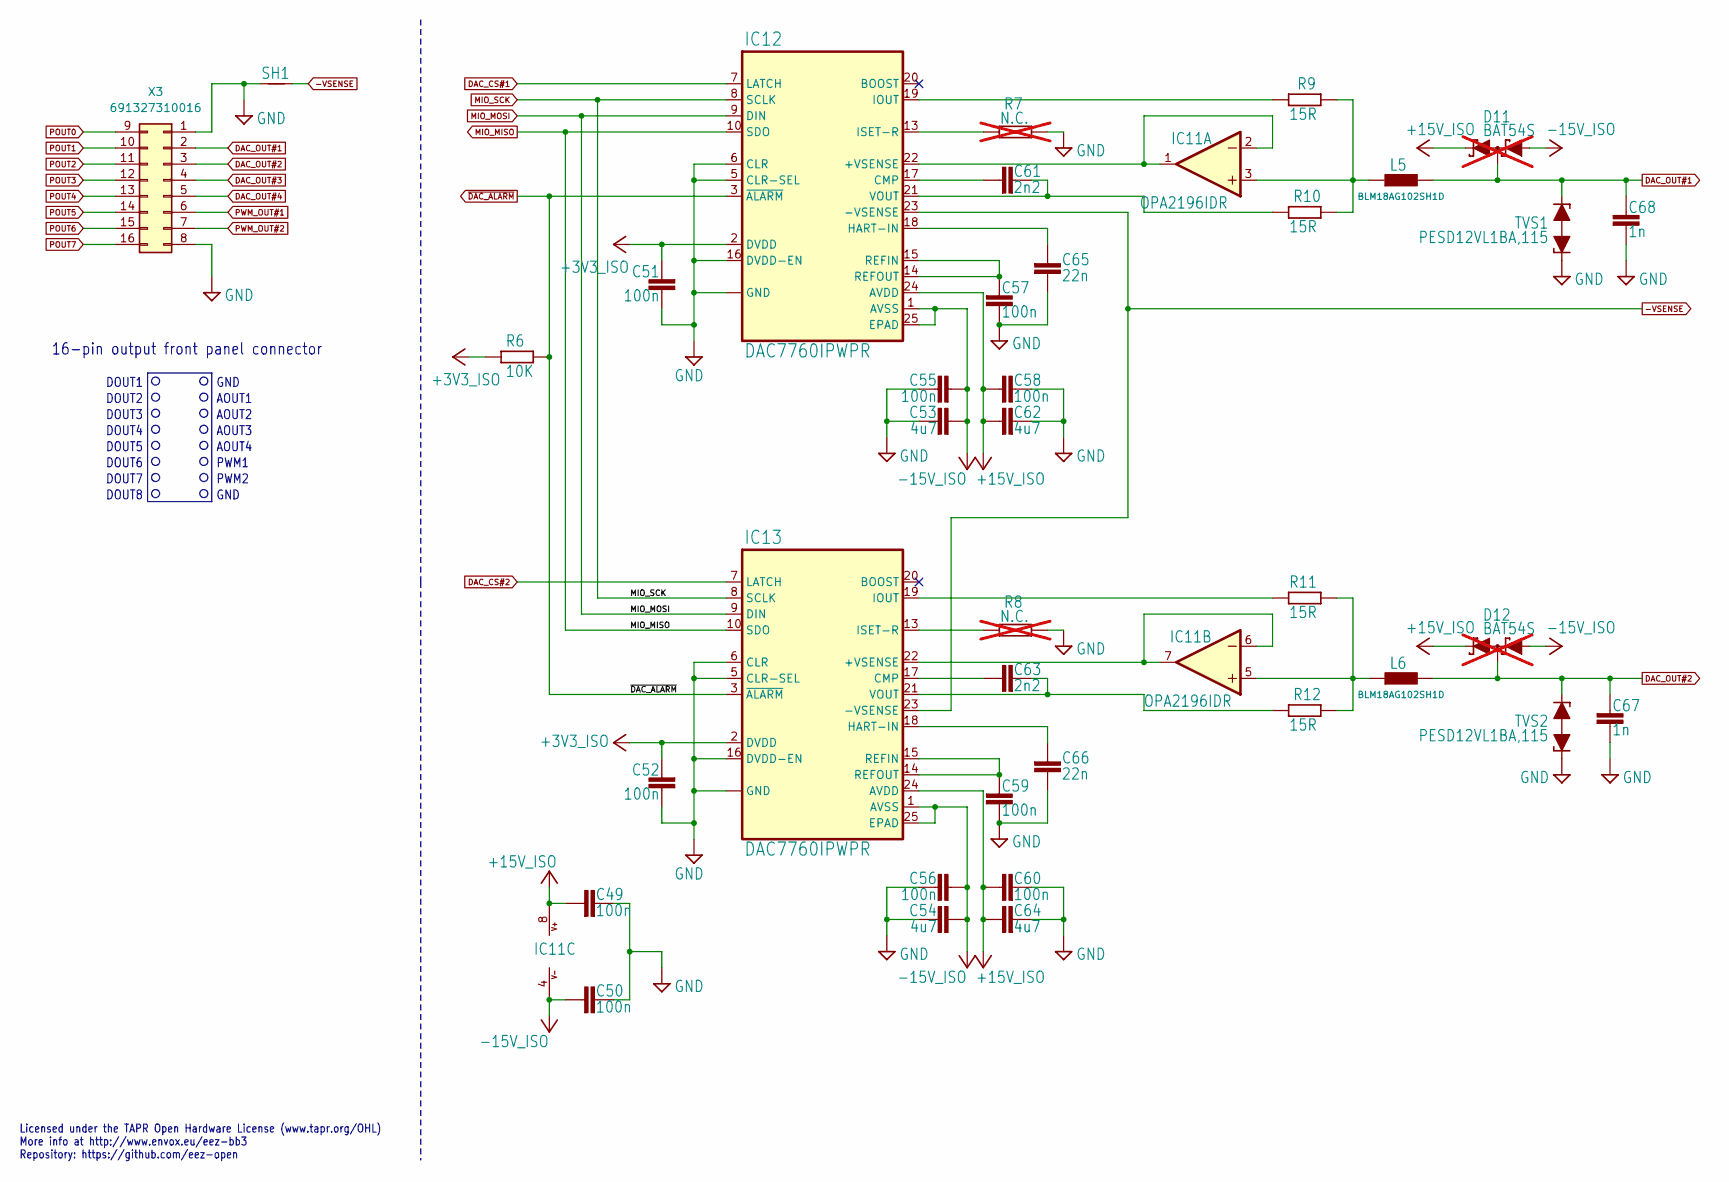
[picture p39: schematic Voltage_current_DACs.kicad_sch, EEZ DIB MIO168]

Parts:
C49, C50, C51, C52, C55, C56, C57, C58, C59, C60: 100n; C_0603_1608Metric; DigiKey 1276-1005-2-ND
C53, C54, C62, C64: 4u7; C_0805_2012Metric; DigiKey 490-14466-1-ND
C61, C63: 2n2; C_0805_2012Metric; DigiKey 732-7840-1-ND
C65, C66: 22n; C_0805_2012Metric; DigiKey 399-1163-1-ND
C67, C68: 1n; C_0805_2012Metric; DigiKey 732-7858-1-ND
D11, D12: BAT54S; SOT23-3; DigiKey 497-2522-1-ND; not fitted
IC11: OPA2196IDR; SOIC127P600X173-8N; DigiKey 296-1282-1-ND
IC12, IC13: DAC7760IPWPR; PWP24; DigiKey 296-37188-1-ND
L5, L6: BLM18AG102SH1D; BEAD0603; DigiKey 490-7809-1-ND
R6: 10K; R_0805_2012Metric; DigiKey CRGH0603F10K
R7, R8: N.C.; R_0805_2012Metric; not fitted
R9, R10, R11, R12: 15R; R_0805_2012Metric; DigiKey RNCP0805FTD15R0CT-ND
SH1: SHORTNOHOLE; NetTie-2_SMD_Pad0.5mm
TVS1, TVS2: PESD12VL1BA,115; SOD-323_PESD; DigiKey 1727-3808-1-ND
X3: 691327310016; DigiKey 732-691327310016-ND

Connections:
+3V3_ISO: C51.1, C52.1, IC12.2 (DVDD), IC13.2 (DVDD), R6.1; also elsewhere on the board
+15V_ISO: C49.1, C58.1, C60.1, C62.2, C64.2, D11.2 (C2), D12.2 (C2), IC11.8 (V+), IC12.24 (AVDD), IC13.24 (AVDD); also elsewhere on the board
-15V_ISO: C50.1, C53.2, C54.2, C55.1, C56.1, D11.1 (A1), D12.1 (A1), IC11.4 (V-), IC12.1 (AVSS), IC12.25 (EPAD), IC13.1 (AVSS), IC13.25 (EPAD); also elsewhere on the board
-VSENSE: IC12.23 (-VSENSE), IC13.23 (-VSENSE), SH1.2; also elsewhere on the board
DAC_CS#1: IC12.7 (LATCH); also elsewhere on the board
DAC_CS#2: IC13.7 (LATCH); also elsewhere on the board
DAC_OUT#1: C68.1, D11.3 (C1A2), L5.2, TVS1.C2 (2), X3.2; also elsewhere on the board
DAC_OUT#2: C67.1, D12.3 (C1A2), L6.2, TVS2.C2 (2), X3.3; also elsewhere on the board
DAC_OUT#3: X3.4; also elsewhere on the board
DAC_OUT#4: X3.5; also elsewhere on the board
GND: C49.2, C50.2, C51.2, C52.2, C53.1, C54.1, C55.2, C56.2, C57.2, C58.2, C59.2, C60.2, C62.1, C64.1, C65.1, C66.1, C67.2, C68.2, IC12.4 (GND), IC12.5 (CLR-SEL), IC12.6 (CLR), IC12.11 (GND), IC12.12 (GND), IC12.16 (DVDD-EN), IC13.4 (GND), IC13.5 (CLR-SEL), IC13.6 (CLR), IC13.11 (GND), IC13.12 (GND), IC13.16 (DVDD-EN), R7.1, R8.1, SH1.1, TVS1.C1 (1), TVS2.C1 (1), X3.1, X3.8; also elsewhere on the board
MIO_MISO: IC12.10 (SDO), IC13.10 (SDO); also elsewhere on the board
MIO_MOSI: IC12.9 (DIN), IC13.9 (DIN); also elsewhere on the board
MIO_SCK: IC12.8 (SCLK), IC13.8 (SCLK); also elsewhere on the board
unnamed: IC11.3 (+IN), L5.1, R9.1, R10.1
unnamed: IC11.1 (OUT), IC11.2 (-IN), IC12.22 (+VSENSE)
unnamed: IC11.5 (+IN), L6.1, R11.1, R12.1
unnamed: IC11.6 (-IN), IC11.7 (OUT), IC13.22 (+VSENSE)
unnamed: C61.2, IC12.17 (CMP)
unnamed: C65.2, IC12.18 (HART-IN)
unnamed: IC12.19 (IOUT), R9.2
unnamed: IC12.13 (ISET-R), R7.2
unnamed: C57.1, IC12.14 (REFOUT), IC12.15 (REFIN)
unnamed: C61.1, IC12.21 (VOUT), R10.2
unnamed: C63.2, IC13.17 (CMP)
unnamed: C66.2, IC13.18 (HART-IN)
unnamed: IC13.19 (IOUT), R11.2
unnamed: IC13.13 (ISET-R), R8.2
unnamed: C59.1, IC13.14 (REFOUT), IC13.15 (REFIN)
unnamed: C63.1, IC13.21 (VOUT), R12.2
POUT0: X3.9; also elsewhere on the board
POUT1: X3.10; also elsewhere on the board
POUT2: X3.11; also elsewhere on the board
POUT3: X3.12; also elsewhere on the board
POUT4: X3.13; also elsewhere on the board
POUT5: X3.14; also elsewhere on the board
POUT6: X3.15; also elsewhere on the board
POUT7: X3.16; also elsewhere on the board
PWM_OUT#1: X3.6; also elsewhere on the board
PWM_OUT#2: X3.7; also elsewhere on the board
~DAC_ALARM: IC12.3 (~ALARM), IC13.3 (~ALARM), R6.2; also elsewhere on the board

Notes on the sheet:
AOUT2
16-pin output front panel connector
AOUT1
DOUT7
PWM1
GND
PWM2
DOUT3
Licensed under the TAPR Open Hardware License (www.tapr.org/OHL) More info at http://www.envox.eu/eez-bb3 Repository: https://github.com/eez-open
DOUT6
DOUT8
DOUT4
AOUT3
AOUT4
DOUT2
DOUT5
DOUT1

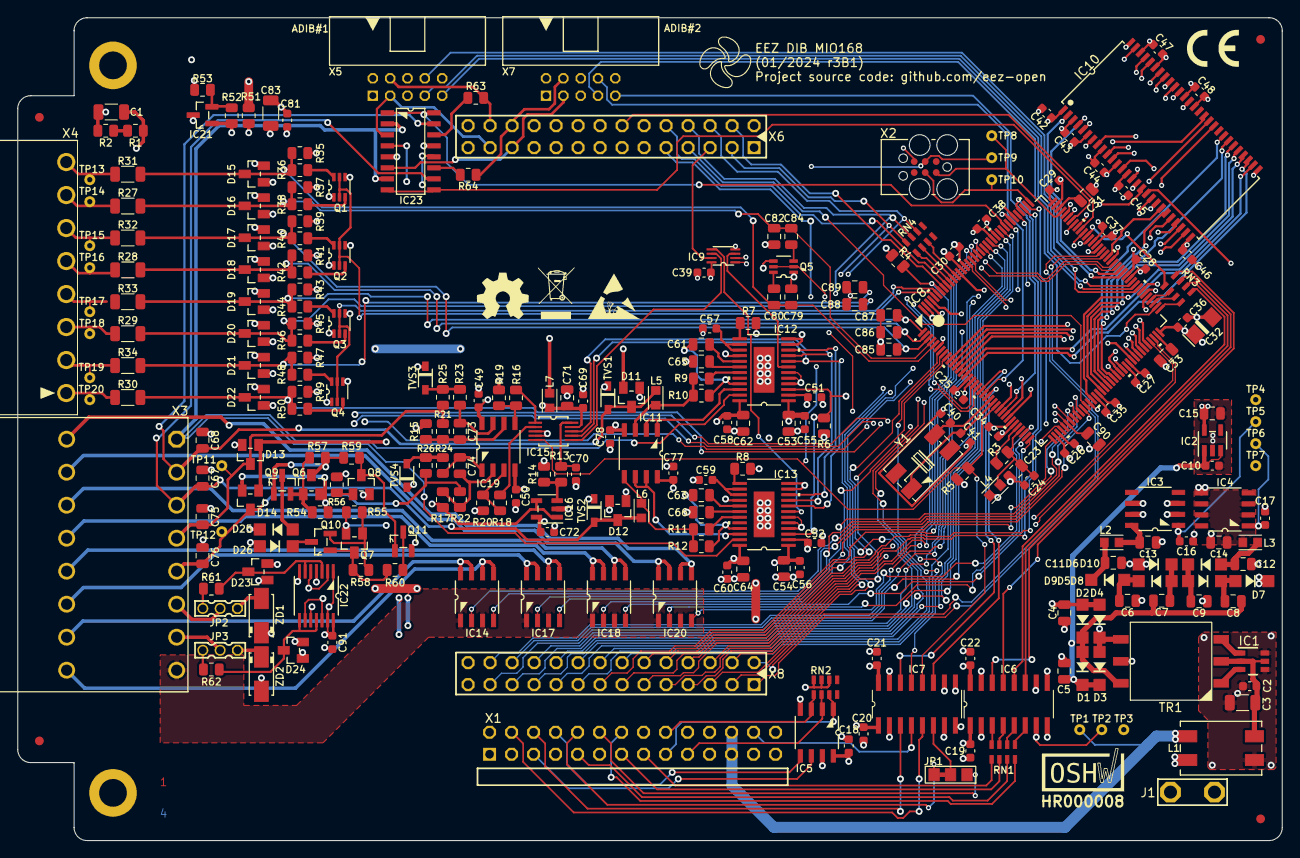
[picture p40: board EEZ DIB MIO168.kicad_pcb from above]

Board: 4 copper layers, 146.0 x 95.0 mm, 279 parts (0 on the bottom side), 261 nets.

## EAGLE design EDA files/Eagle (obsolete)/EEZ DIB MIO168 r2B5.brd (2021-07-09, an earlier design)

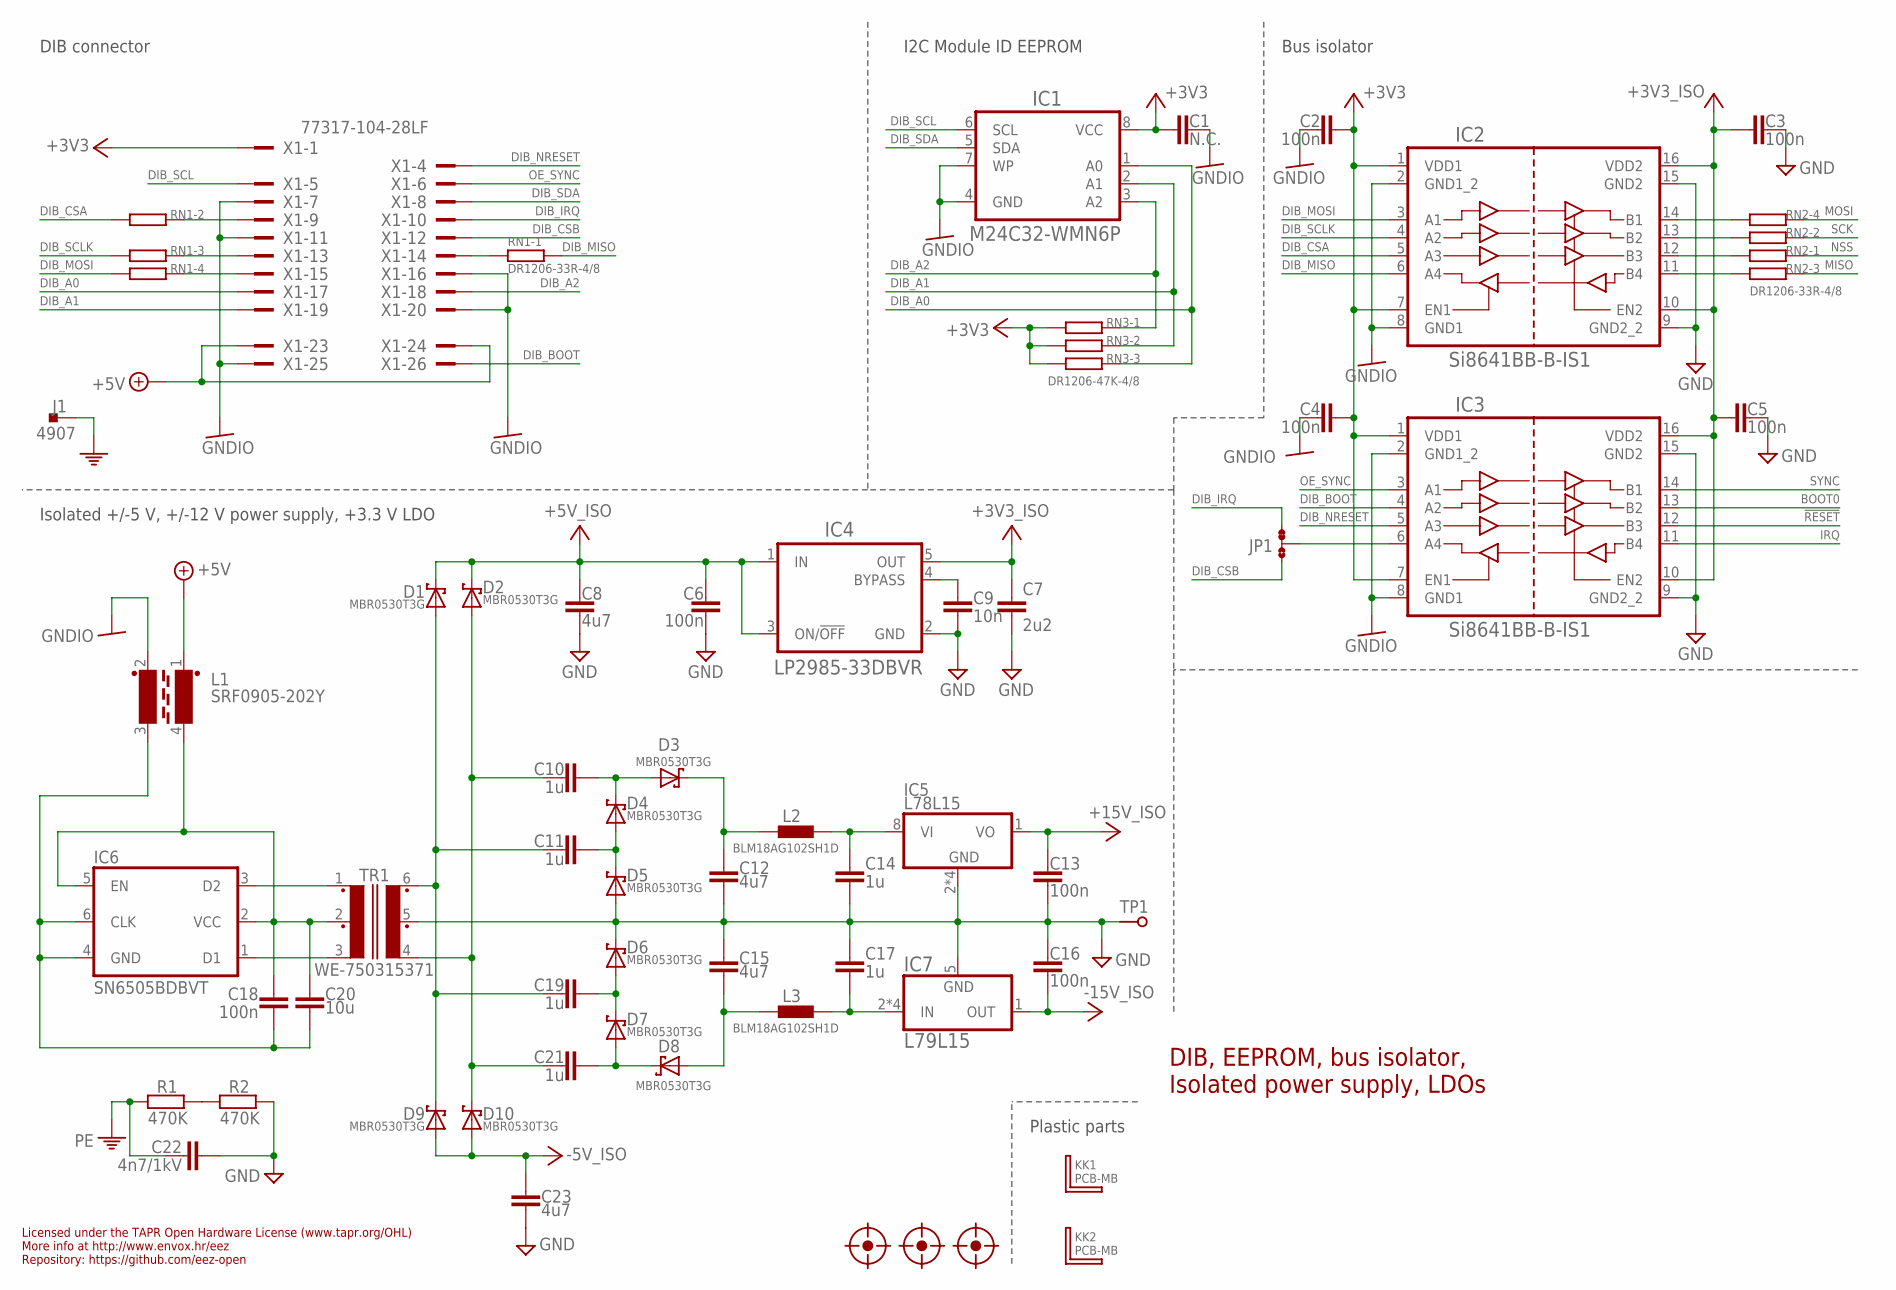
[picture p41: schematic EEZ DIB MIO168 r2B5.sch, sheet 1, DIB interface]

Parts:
C1: N.C.; C0603
C2, C3, C4, C5, C6, C13, C16, C18: 100n; C0603
C7: 2u2; C0805
C8, C12, C15, C23: 4u7; C0805
C9: 10n; C0805
C10, C11, C14, C17, C19, C21: 1u; C0805
C20: 10u; C1206
C22: 4n7/1kV; C1812
D1, D2, D3, D4, D5, D6, D7, D8, D9, D10: MBR0530T3G; SOD123
FM1, FM2, FM3: FIDUCIAL_2; FIDUCIAL_DUAL
IC1: M24C32-WMN6P; SOIC127P600X173-8N
IC2, IC3: Si8641BB-B-IS1; SOIC-16
IC4: LP2985-33DBVR; SOT95P270X145-5N
IC5: L78L15; SOIC127P600X173-8N
IC6: SN6505BDBVT; DBV0006A_N
IC7: L79L15; SOIC127P600X173-8N
J1: 4907; PCB_TAB-4907
JP1: JP3-CUT-0805-ROTATED; JP3-0805-CUT2
KK1, KK2: PCB-MB
L1: SRF0905-202Y; SRF0905
L2, L3: BLM18AG102SH1D; BEAD0603
R1, R2: 470K; R0805
RN1, RN2: DR1206-33R-4/8; CAY16
RN3: DR1206-47K-4/8; CAY16
TP1: PCB_TEST_TABSHIELD; PCB_SHIELD_TAB
TR1: WE-750315371; MURATA_78615
X1: 77317-104-28LF

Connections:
!RESET: IC3.12 (B3); also elsewhere on the board
+3V3: C1.2, C2.1, C4.1, IC1.8 (VCC), IC2.1 (VDD1), IC2.7 (EN1), IC3.1 (VDD1), IC3.7 (EN1), RN3.6 (2), RN3.7 (2), RN3.8 (2), X1.1
+3V3_ISO: C3.2, C5.2, C7.1, IC2.10 (EN2), IC2.16 (VDD2), IC3.10 (EN2), IC3.16 (VDD2), IC4.5 (OUT); also elsewhere on the board
+5V: L1.1, X1.23, X1.24
+5V_ISO: C6.1, C8.2, D1.C, D2.C, IC4.1 (IN), IC4.3 (ON/!OFF); also elsewhere on the board
+15V_ISO: C13.1, IC5.1 (VO); also elsewhere on the board
-5V_ISO: C23.2, D9.A, D10.A; also elsewhere on the board
-15V_IN: C17.1, IC7.2 (IN), IC7.3 (IN), IC7.6 (IN), IC7.7 (IN), L3.P$2 (2)
-15V_ISO: C16.2, IC7.1 (OUT); also elsewhere on the board
BOOT0: IC3.13 (B2); also elsewhere on the board
DIB_A0: IC1.1 (A0), RN3.3 (1), X1.17
DIB_A1: IC1.2 (A1), RN3.2 (1), X1.19
DIB_A2: IC1.3 (A2), RN3.1, X1.18
DIB_BOOT: IC3.4 (A2), X1.26
DIB_CSA: IC2.5 (A3), RN1.2 (1)
DIB_CSB: JP1.NO, X1.12
DIB_IRQ: JP1.NC, X1.10
DIB_MISO: IC2.6 (A4), RN1.1
DIB_MOSI: IC2.3 (A1), RN1.4 (1)
DIB_NRESET: IC3.5 (A3), X1.4
DIB_SCL: IC1.6 (SCL), X1.5
DIB_SCLK: IC2.4 (A2), RN1.3 (1)
DIB_SDA: IC1.5 (SDA), X1.8
GND: C3.1, C5.1, C6.2, C7.2, C8.1, C9.1, C12.2, C13.2, C14.1, C15.1, C16.1, C17.2, C22.2, C23.1, D5.A, D6.C, IC2.9 (GND2_2), IC2.15 (GND2), IC3.9 (GND2_2), IC3.15 (GND2), IC4.2 (GND), IC5.2 (GND), IC5.3 (GND), IC5.6 (GND), IC5.7 (GND), IC7.5 (GND), R2.2, TP1.1, TR1.5; also elsewhere on the board
GNDIO: C1.1, C2.2, C4.2, IC1.4 (GND), IC1.7 (WP), IC2.2 (GND1_2), IC2.8 (GND1), IC3.2 (GND1_2), IC3.8 (GND1), L1.2, X1.7, X1.11, X1.16, X1.20, X1.25
IRQ: IC3.11 (B4); also elsewhere on the board
MISO: RN2.6 (2); also elsewhere on the board
MOSI: RN2.5 (2); also elsewhere on the board
unnamed: IC3.6 (A4), JP1.COM
unnamed: IC2.14 (B1), RN2.4 (1)
unnamed: R1.2, R2.1
unnamed: C11.1, D4.A, D5.C
unnamed: IC6.3 (D2), TR1.1
unnamed: IC6.1 (D1), TR1.3
unnamed: C11.2, C19.2, D1.A, D9.C, TR1.6
unnamed: RN1.7 (2), X1.9
unnamed: C10.2, C21.2, D2.A, D10.C, TR1.4
unnamed: IC2.11 (B4), RN2.3 (1)
unnamed: C10.1, D3.A, D4.C
unnamed: RN1.6 (2), X1.13
unnamed: RN1.8 (2), X1.14
unnamed: RN1.5 (2), X1.15
unnamed: C19.1, D6.A, D7.C
unnamed: C21.1, D7.A, D8.C
unnamed: C9.2, IC4.4 (BYPASS)
unnamed: C14.2, IC5.8 (VI), L2.P$2 (2)
unnamed: IC2.13 (B2), RN2.2 (1)
unnamed: IC2.12 (B3), RN2.1
unnamed: C15.2, D8.A, L3.P$1 (1)
unnamed: C12.1, D3.C, L2.P$1 (1)
NSS: RN2.8 (2); also elsewhere on the board
OE_SYNC: IC3.3 (A1), X1.6
PE: C22.1, J1.1, J1.2, R1.1
SCK: RN2.7 (2); also elsewhere on the board
SN_GND: C18.2, C20.1, IC6.4 (GND), IC6.6 (CLK), L1.3
SN_VCC: C18.1, C20.2, IC6.2 (VCC), IC6.5 (EN), L1.4, TR1.2
SYNC: IC3.14 (B1); also elsewhere on the board

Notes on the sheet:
Licensed under the TAPR Open Hardware License (www.tapr.org/OHL)
Repository: https://github.com/eez-open
More info at http://www.envox.hr/eez
DIB, EEPROM, bus isolator, Isolated power supply, LDOs
Plastic parts
I2C Module ID EEPROM
Bus isolator
Isolated +/-5 V, +/-12 V power supply, +3.3 V LDO
DIB connector

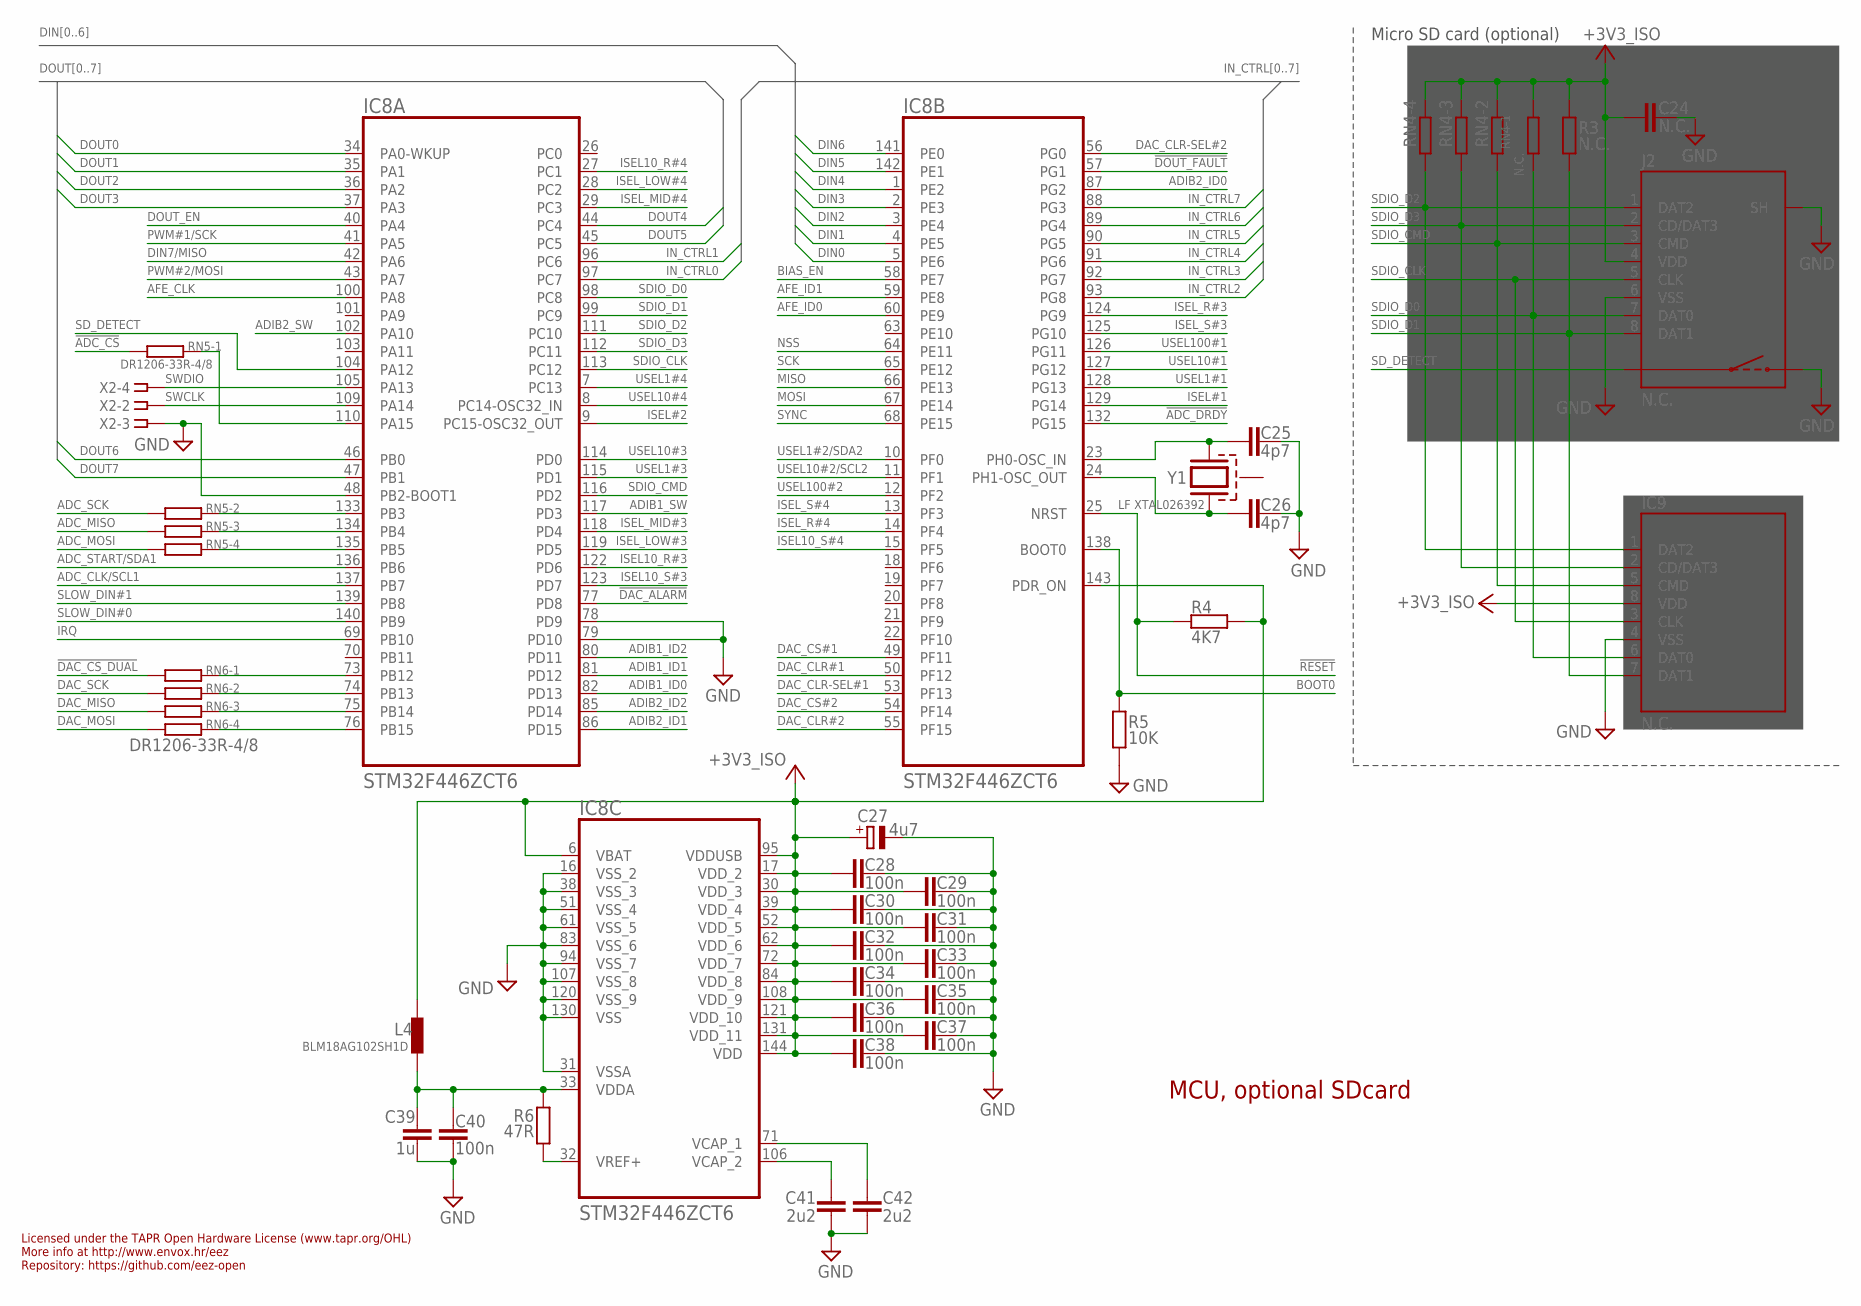
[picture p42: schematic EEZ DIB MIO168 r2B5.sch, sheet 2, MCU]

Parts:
C24: N.C.; C0805
C25, C26: 4p7; C0603
C27: 4u7; EC1206
C28, C29, C30, C31, C32, C33, C34, C35, C36, C37, C38, C40: 100n; C0603
C39: 1u; C0805
C41, C42: 2u2; C0805
IC8: STM32F446ZCT6; LQFP-144
IC9: N.C.; LGA8
J2: N.C.; 5033981892
L4: BLM18AG102SH1D; BEAD0603
R3: N.C.; R0805
R4: 4K7; R0805
R5: 10K; R0805
R6: 47R; R0805
RN4: N.C.; CAY16
RN5, RN6: DR1206-33R-4/8; CAY16
X2: N.C.; SSW-106-02-S-S
Y1: LF XTAL026392; 12SMX(B)

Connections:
!ADC_CS: RN5.1; also elsewhere on the board
!ADC_DRDY: IC8.132 (PG15); also elsewhere on the board
!DAC_ALARM: IC8.77 (PD8); also elsewhere on the board
!DAC_CS_DUAL: RN6.1; also elsewhere on the board
!DOUT_FAULT: IC8.57 (PG1); also elsewhere on the board
!RESET: IC8.25 (NRST), R4.2; also elsewhere on the board
+3V3_ISO: C24.1, C27.+, C28.1, C29.1, C30.1, C31.1, C32.1, C33.1, C34.1, C35.1, C36.1, C37.1, C38.1, IC8.6 (VBAT), IC8.17 (VDD_2), IC8.30 (VDD_3), IC8.39 (VDD_4), IC8.52 (VDD_5), IC8.62 (VDD_6), IC8.72 (VDD_7), IC8.84 (VDD_8), IC8.95 (VDDUSB), IC8.108 (VDD_9), IC8.121 (VDD_10), IC8.131 (VDD_11), IC8.143 (PDR_ON), IC8.144 (VDD), IC9.8 (VDD), J2.4 (VDD), L4.P$1 (1), R3.1, R4.1, RN4.1, RN4.2 (1), RN4.3 (1), RN4.4 (1); also elsewhere on the board
ADC_CLK/SCL1: IC8.137 (PB7); also elsewhere on the board
ADC_MISO: RN5.3 (1); also elsewhere on the board
ADC_MOSI: RN5.4 (1); also elsewhere on the board
ADC_SCK: RN5.2 (1); also elsewhere on the board
ADC_START/SDA1: IC8.136 (PB6); also elsewhere on the board
ADIB1_ID0: IC8.82 (PD13); also elsewhere on the board
ADIB1_ID1: IC8.81 (PD12); also elsewhere on the board
ADIB1_ID2: IC8.80 (PD11); also elsewhere on the board
ADIB1_SW: IC8.117 (PD3); also elsewhere on the board
ADIB2_ID0: IC8.87 (PG2); also elsewhere on the board
ADIB2_ID1: IC8.86 (PD15); also elsewhere on the board
ADIB2_ID2: IC8.85 (PD14); also elsewhere on the board
ADIB2_SW: IC8.102 (PA10); also elsewhere on the board
AFE_CLK: IC8.100 (PA8); also elsewhere on the board
AFE_ID0: IC8.60 (PE9); also elsewhere on the board
AFE_ID1: IC8.59 (PE8); also elsewhere on the board
BIAS_EN: IC8.58 (PE7); also elsewhere on the board
BOOT0: IC8.138 (BOOT0), R5.2; also elsewhere on the board
DAC_CLR#1: IC8.50 (PF12); also elsewhere on the board
DAC_CLR#2: IC8.55 (PF15); also elsewhere on the board
DAC_CLR-SEL#1: IC8.53 (PF13); also elsewhere on the board
DAC_CLR-SEL#2: IC8.56 (PG0); also elsewhere on the board
DAC_CS#1: IC8.49 (PF11); also elsewhere on the board
DAC_CS#2: IC8.54 (PF14); also elsewhere on the board
DAC_MISO: RN6.3 (1); also elsewhere on the board
DAC_MOSI: RN6.4 (1); also elsewhere on the board
DAC_SCK: RN6.2 (1); also elsewhere on the board
DIN0: IC8.5 (PE6); also elsewhere on the board
DIN1: IC8.4 (PE5); also elsewhere on the board
DIN2: IC8.3 (PE4); also elsewhere on the board
DIN3: IC8.2 (PE3); also elsewhere on the board
DIN4: IC8.1 (PE2); also elsewhere on the board
DIN5: IC8.142 (PE1); also elsewhere on the board
DIN6: IC8.141 (PE0); also elsewhere on the board
DIN7/MISO: IC8.42 (PA6); also elsewhere on the board
DOUT0: IC8.34 (PA0-WKUP); also elsewhere on the board
DOUT1: IC8.35 (PA1); also elsewhere on the board
DOUT2: IC8.36 (PA2); also elsewhere on the board
DOUT3: IC8.37 (PA3); also elsewhere on the board
DOUT4: IC8.44 (PC4); also elsewhere on the board
DOUT5: IC8.45 (PC5); also elsewhere on the board
DOUT6: IC8.46 (PB0); also elsewhere on the board
DOUT7: IC8.47 (PB1); also elsewhere on the board
DOUT_EN: IC8.40 (PA4); also elsewhere on the board
GND: C24.2, C25.1, C26.1, C27.-, C28.2, C29.2, C30.2, C31.2, C32.2, C33.2, C34.2, C35.2, C36.2, C37.2, C38.2, C39.2, C40.2, C41.1, C42.1, IC8.16 (VSS_2), IC8.31 (VSSA), IC8.38 (VSS_3), IC8.48 (PB2-BOOT1), IC8.51 (VSS_4), IC8.61 (VSS_5), IC8.78 (PD9), IC8.79 (PD10), IC8.83 (VSS_6), IC8.94 (VSS_7), IC8.107 (VSS_8), IC8.120 (VSS_9), IC8.130 (VSS), IC9.4 (VSS), J2.6 (VSS), J2.S (SH), J2.S1 (SH), J2.S2 (SH), J2.SW2, R5.1, X2.3; also elsewhere on the board
IN_CTRL0: IC8.97 (PC7); also elsewhere on the board
IN_CTRL1: IC8.96 (PC6); also elsewhere on the board
IN_CTRL2: IC8.93 (PG8); also elsewhere on the board
IN_CTRL3: IC8.92 (PG7); also elsewhere on the board
IN_CTRL4: IC8.91 (PG6); also elsewhere on the board
IN_CTRL5: IC8.90 (PG5); also elsewhere on the board
IN_CTRL6: IC8.89 (PG4); also elsewhere on the board
IN_CTRL7: IC8.88 (PG3); also elsewhere on the board
IRQ: IC8.69 (PB10); also elsewhere on the board
ISEL10_R#3: IC8.122 (PD6); also elsewhere on the board
ISEL10_R#4: IC8.27 (PC1); also elsewhere on the board
ISEL10_S#3: IC8.123 (PD7); also elsewhere on the board
ISEL10_S#4: IC8.15 (PF5); also elsewhere on the board
ISEL#1: IC8.129 (PG14); also elsewhere on the board
ISEL#2: IC8.9 (PC15-OSC32_OUT); also elsewhere on the board
ISEL_LOW#3: IC8.119 (PD5); also elsewhere on the board
ISEL_LOW#4: IC8.28 (PC2); also elsewhere on the board
ISEL_MID#3: IC8.118 (PD4); also elsewhere on the board
ISEL_MID#4: IC8.29 (PC3); also elsewhere on the board
ISEL_R#3: IC8.124 (PG9); also elsewhere on the board
ISEL_R#4: IC8.14 (PF4); also elsewhere on the board
ISEL_S#3: IC8.125 (PG10); also elsewhere on the board
ISEL_S#4: IC8.13 (PF3); also elsewhere on the board
MISO: IC8.66 (PE13); also elsewhere on the board
MOSI: IC8.67 (PE14); also elsewhere on the board
unnamed: IC8.110 (PA15), RN5.8 (2)
unnamed: IC8.133 (PB3), RN5.7 (2)
unnamed: IC8.134 (PB4), RN5.6 (2)
unnamed: C41.2, IC8.106 (VCAP_2)
unnamed: IC8.135 (PB5), RN5.5 (2)
unnamed: C42.2, IC8.71 (VCAP_1)
unnamed: C39.1, C40.1, IC8.33 (VDDA), L4.P$2 (2), R6.1
unnamed: IC8.32 (VREF+), R6.2
unnamed: IC8.73 (PB12), RN6.8 (2)
unnamed: IC8.74 (PB13), RN6.7 (2)
unnamed: IC8.75 (PB14), RN6.6 (2)
unnamed: IC8.76 (PB15), RN6.5 (2)
NSS: IC8.64 (PE11); also elsewhere on the board
PWM#1/SCK: IC8.41 (PA5); also elsewhere on the board
PWM#2/MOSI: IC8.43 (PA7); also elsewhere on the board
RCC_OSC_IN: C25.2, IC8.23 (PH0-OSC_IN), Y1.3 (2)
RCC_OSC_OUT: C26.2, IC8.24 (PH1-OSC_OUT), Y1.1
SCK: IC8.65 (PE12); also elsewhere on the board
SDIO_CLK: IC8.113 (PC12), IC9.3 (CLK), J2.5 (CLK)
SDIO_CMD: IC8.116 (PD2), IC9.5 (CMD), J2.3 (CMD), RN4.7 (2)
SDIO_D0: IC8.98 (PC8), IC9.6 (DAT0), J2.7 (DAT0), RN4.8 (2)
SDIO_D1: IC8.99 (PC9), IC9.7 (DAT1), J2.8 (DAT1), R3.2
SDIO_D2: IC8.111 (PC10), IC9.1 (DAT2), J2.1 (DAT2), RN4.5 (2)
SDIO_D3: IC8.112 (PC11), IC9.2 (CD/DAT3), J2.2 (CD/DAT3), RN4.6 (2)
SD_DETECT: IC8.104 (PA12), J2.SW1
SLOW_DIN#0: IC8.140 (PB9); also elsewhere on the board
SLOW_DIN#1: IC8.139 (PB8); also elsewhere on the board
SWCLK: IC8.109 (PA14), X2.2
SWDIO: IC8.105 (PA13), X2.4
SYNC: IC8.68 (PE15); also elsewhere on the board
USEL1#1: IC8.128 (PG13); also elsewhere on the board
USEL1#2/SDA2: IC8.10 (PF0); also elsewhere on the board
USEL1#3: IC8.115 (PD1); also elsewhere on the board
USEL1#4: IC8.7 (PC13); also elsewhere on the board
USEL10#1: IC8.127 (PG12); also elsewhere on the board
USEL10#2/SCL2: IC8.11 (PF1); also elsewhere on the board
USEL10#3: IC8.114 (PD0); also elsewhere on the board
USEL10#4: IC8.8 (PC14-OSC32_IN); also elsewhere on the board
USEL100#1: IC8.126 (PG11); also elsewhere on the board
USEL100#2: IC8.12 (PF2); also elsewhere on the board

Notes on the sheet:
Licensed under the TAPR Open Hardware License (www.tapr.org/OHL)
Repository: https://github.com/eez-open
More info at http://www.envox.hr/eez
MCU, optional SDcard
Micro SD card (optional)

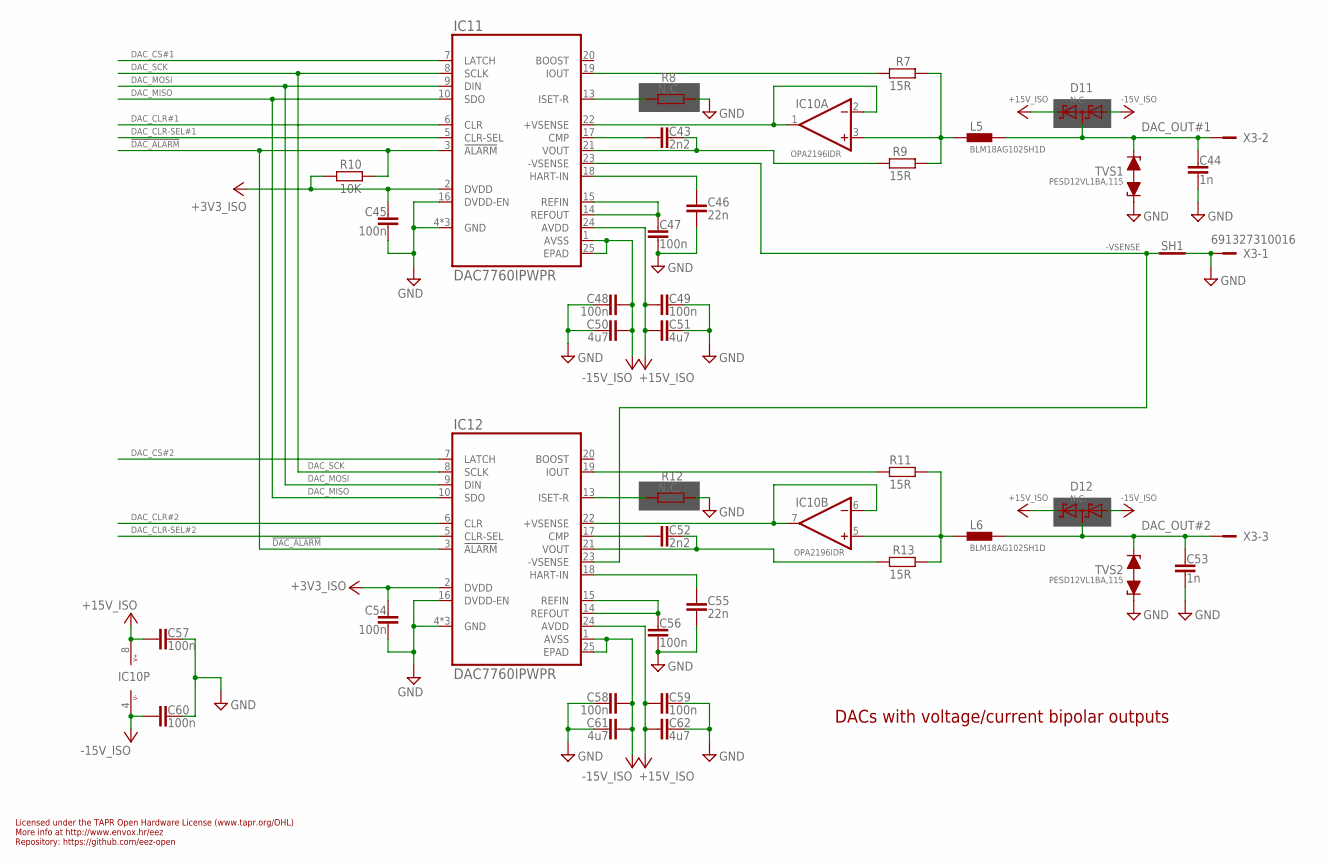
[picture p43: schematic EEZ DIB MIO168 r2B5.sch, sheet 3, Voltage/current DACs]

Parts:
C43, C52: 2n2; C0805
C44, C53: 1n; C0805
C45, C47, C48, C49, C54, C56, C57, C58, C59, C60: 100n; C0603
C46, C55: 22n; C0805
C50, C51, C61, C62: 4u7; C0805
D11, D12: N.C.; SOT23
IC10: OPA2196IDR; SOIC127P600X173-8N
IC11, IC12: DAC7760IPWPR; PWP24
L5, L6: BLM18AG102SH1D; BEAD0603
R7, R9, R11, R13: 15R; R0805
R8, R12: N.C.; R0805
R10: 10K; R0805
SH1: SHORTNOHOLE; SHORT_NOHOLE
TVS1, TVS2: PESD12VL1BA,115; SOD323-BIDIR
X3: 691327310016

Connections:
!DAC_ALARM: IC11.3 (!ALARM), IC12.3 (!ALARM), R10.2; also elsewhere on the board
+3V3_ISO: C45.1, C54.1, IC11.2 (DVDD), IC12.2 (DVDD), R10.1; also elsewhere on the board
+15V_ISO: C49.1, C51.2, C57.1, C59.1, C62.2, D11.2 (C2), D12.2 (C2), IC10.8 (V+), IC11.24 (AVDD), IC12.24 (AVDD); also elsewhere on the board
+VSENSE1: IC10.1 (OUT), IC10.2 (-IN), IC11.22 (+VSENSE)
+VSENSE2: IC10.6 (-IN), IC10.7 (OUT), IC12.22 (+VSENSE)
-15V_ISO: C48.1, C50.2, C58.1, C60.1, C61.2, D11.1 (A1), D12.1 (A1), IC10.4 (V-), IC11.1 (AVSS), IC11.25 (EPAD), IC12.1 (AVSS), IC12.25 (EPAD); also elsewhere on the board
-VSENSE: IC11.23 (-VSENSE), IC12.23 (-VSENSE), SH1.2 (GND_B); also elsewhere on the board
DAC_CLR#1: IC11.6 (CLR); also elsewhere on the board
DAC_CLR#2: IC12.6 (CLR); also elsewhere on the board
DAC_CLR-SEL#1: IC11.5 (CLR-SEL); also elsewhere on the board
DAC_CLR-SEL#2: IC12.5 (CLR-SEL); also elsewhere on the board
DAC_CS#1: IC11.7 (LATCH); also elsewhere on the board
DAC_CS#2: IC12.7 (LATCH); also elsewhere on the board
DAC_MISO: IC11.10 (SDO), IC12.10 (SDO); also elsewhere on the board
DAC_MOSI: IC11.9 (DIN), IC12.9 (DIN); also elsewhere on the board
DAC_OUT#1: C44.1, D11.3 (C1A2), L5.P$2 (2), TVS1.C2 (2), X3.2; also elsewhere on the board
DAC_OUT#2: C53.1, D12.3 (C1A2), L6.P$2 (2), TVS2.C2 (2), X3.3; also elsewhere on the board
DAC_SCK: IC11.8 (SCLK), IC12.8 (SCLK); also elsewhere on the board
GND: C44.2, C45.2, C46.1, C47.2, C48.2, C49.2, C50.1, C51.1, C53.2, C54.2, C55.1, C56.2, C57.2, C58.2, C59.2, C60.2, C61.1, C62.1, IC11.4 (GND), IC11.11 (GND), IC11.12 (GND), IC11.16 (DVDD-EN), IC12.4 (GND), IC12.11 (GND), IC12.12 (GND), IC12.16 (DVDD-EN), R8.1, R12.1, SH1.1 (GND_A), TVS1.C1 (1), TVS2.C1 (1), X3.1; also elsewhere on the board
HART#1: C46.2, IC11.18 (HART-IN)
HART#2: C55.2, IC12.18 (HART-IN)
unnamed: C52.2, IC12.17 (CMP)
unnamed: C52.1, IC12.21 (VOUT), R13.2
unnamed: IC10.5 (+IN), L6.P$1 (1), R11.1, R13.1
unnamed: IC12.19 (IOUT), R11.2
unnamed: C56.1, IC12.14 (REFOUT), IC12.15 (REFIN)
unnamed: C43.2, IC11.17 (CMP)
unnamed: IC10.3 (+IN), L5.P$1 (1), R7.1, R9.1
unnamed: C47.1, IC11.14 (REFOUT), IC11.15 (REFIN)
unnamed: IC12.13 (ISET-R), R12.2
unnamed: IC11.13 (ISET-R), R8.2
unnamed: C43.1, IC11.21 (VOUT), R9.2
unnamed: IC11.19 (IOUT), R7.2

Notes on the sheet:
Licensed under the TAPR Open Hardware License (www.tapr.org/OHL)
Repository: https://github.com/eez-open
More info at http://www.envox.hr/eez
DACs with voltage/current bipolar outputs

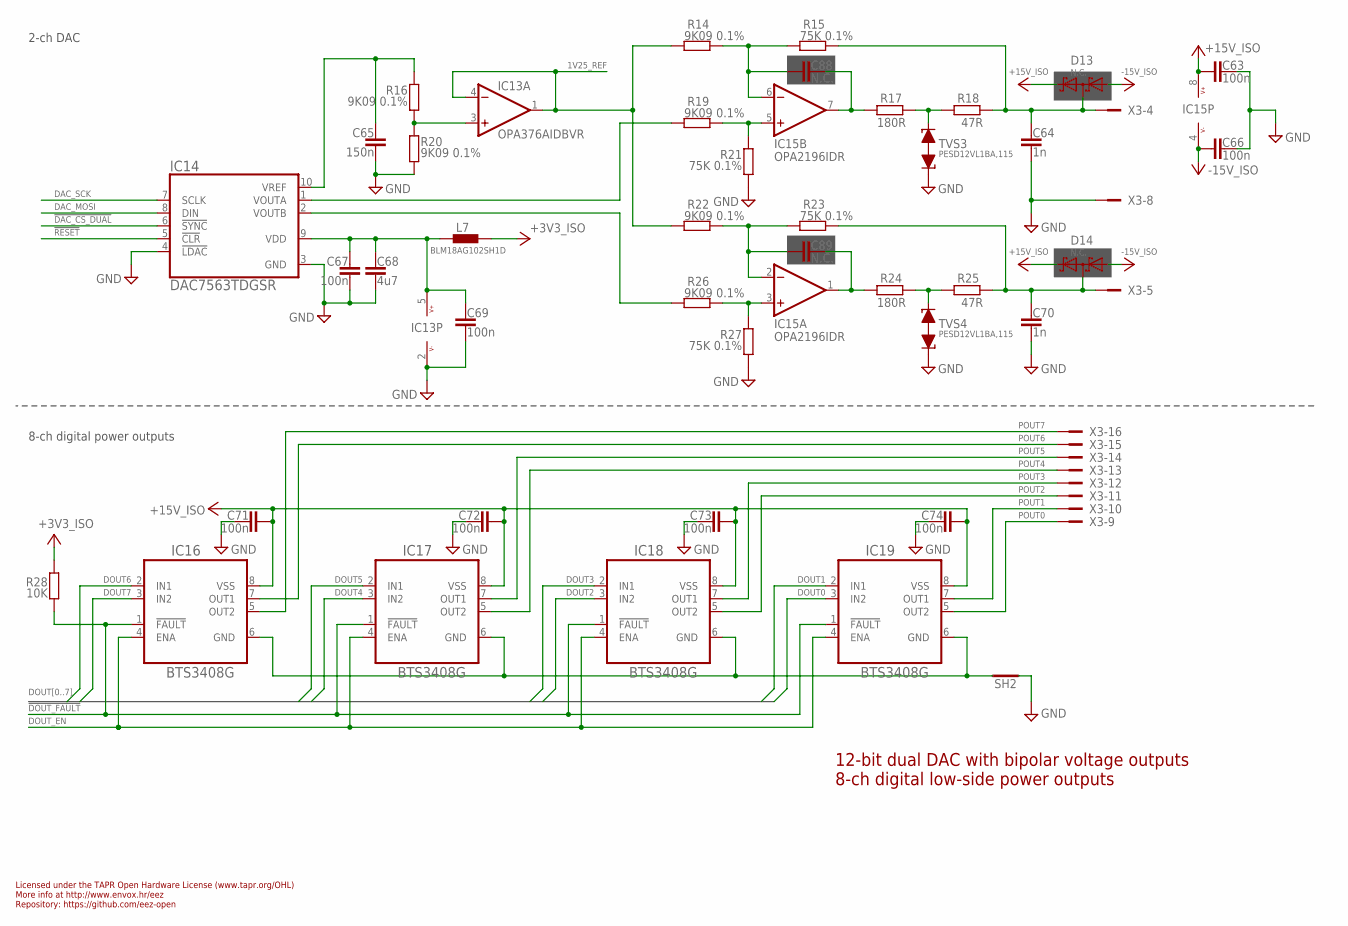
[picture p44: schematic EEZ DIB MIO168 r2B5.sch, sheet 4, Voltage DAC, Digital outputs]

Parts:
C63, C66, C67, C69, C71, C72, C73, C74: 100n; C0603
C64, C70: 1n; C0805
C65: 150n; C0805
C68: 4u7; C0805
C88, C89: N.C.; C0805
D13, D14: N.C.; SOT23
IC13: OPA376AIDBVR; DBV5
IC14: DAC7563TDGSR; DGS10
IC15: OPA2196IDR; SOIC127P600X173-8N
IC16, IC17, IC18, IC19: BTS3408G; SOIC127P600X173-8N
L7: BLM18AG102SH1D; BEAD0603
R14, R16, R19, R20, R22, R26: 9K09 0.1%; R0805
R15, R21, R23, R27: 75K 0.1%; R0805
R17, R24: 180R; R0805
R18, R25: 47R; R0805
R28: 10K; R0805
SH2: SHORTNOHOLE; SHORT_NOHOLE
TVS3, TVS4: PESD12VL1BA,115; SOD323-BIDIR
X3: 691327310016

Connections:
1V25_REF: IC13.1 (OUT), IC13.4 (-IN), R14.2, R22.2
2V5_REF: C65.2, IC14.10 (VREF), R16.1
!DAC_CS_DUAL: IC14.6 (!SYNC); also elsewhere on the board
!DOUT_FAULT: IC16.1 (!FAULT), IC17.1 (!FAULT), IC18.1 (!FAULT), IC19.1 (!FAULT), R28.2; also elsewhere on the board
!RESET: IC14.5 (!CLR); also elsewhere on the board
+3V3_ISO: L7.P$2 (2), R28.1; also elsewhere on the board
+15V_ISO: C63.1, C71.2, C72.2, C73.2, C74.2, D13.2 (C2), D14.2 (C2), IC15.8 (V+), IC16.8 (VSS), IC17.8 (VSS), IC18.8 (VSS), IC19.8 (VSS); also elsewhere on the board
-15V_ISO: C66.1, D13.1 (A1), D14.1 (A1), IC15.4 (V-); also elsewhere on the board
DAC_MOSI: IC14.8 (DIN); also elsewhere on the board
DAC_SCK: IC14.7 (SCLK); also elsewhere on the board
DOUT0: IC19.3 (IN2); also elsewhere on the board
DOUT1: IC19.2 (IN1); also elsewhere on the board
DOUT2: IC18.3 (IN2); also elsewhere on the board
DOUT3: IC18.2 (IN1); also elsewhere on the board
DOUT4: IC17.3 (IN2); also elsewhere on the board
DOUT5: IC17.2 (IN1); also elsewhere on the board
DOUT6: IC16.2 (IN1); also elsewhere on the board
DOUT7: IC16.3 (IN2); also elsewhere on the board
DOUT_EN: IC16.4 (ENA), IC17.4 (ENA), IC18.4 (ENA), IC19.4 (ENA); also elsewhere on the board
GND: C63.2, C64.2, C65.1, C66.2, C67.2, C68.1, C69.2, C70.2, C71.1, C72.1, C73.1, C74.1, IC13.2 (V-), IC14.3 (GND), IC14.4 (!LDAC), R20.2, R21.2, R27.2, SH2.1 (GND_A), TVS3.C1 (1), TVS4.C1 (1), X3.8; also elsewhere on the board
ISET1: R17.2, R18.1, TVS3.C2 (2)
ISET2: R24.2, R25.1, TVS4.C2 (2)
unnamed: IC16.6 (GND), IC17.6 (GND), IC18.6 (GND), IC19.6 (GND), SH2.2 (GND_B)
unnamed: IC15.5 (+IN), R19.1, R21.1
unnamed: C88.1, IC15.6 (-IN), R14.1, R15.2
unnamed: C88.2, IC15.7 (OUT), R17.1
unnamed: IC15.3 (+IN), R26.1, R27.1
unnamed: C89.1, IC15.2 (-IN), R22.1, R23.2
unnamed: C89.2, IC15.1 (OUT), R24.1
unnamed: IC13.3 (+IN), R16.2, R20.1
unnamed: IC14.1 (VOUTA), R19.2
unnamed: IC14.2 (VOUTB), R26.2
unnamed: C67.1, C68.2, C69.1, IC13.5 (V+), IC14.9 (VDD), L7.P$1 (1)
unnamed: C70.1, D14.3 (C1A2), R23.1, R25.2, X3.5
unnamed: C64.1, D13.3 (C1A2), R15.1, R18.2, X3.4
POUT0: IC19.5 (OUT2), X3.9
POUT1: IC19.7 (OUT1), X3.10
POUT2: IC18.5 (OUT2), X3.11
POUT3: IC18.7 (OUT1), X3.12
POUT4: IC17.5 (OUT2), X3.13
POUT5: IC17.7 (OUT1), X3.14
POUT6: IC16.7 (OUT1), X3.15
POUT7: IC16.5 (OUT2), X3.16

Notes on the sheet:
Licensed under the TAPR Open Hardware License (www.tapr.org/OHL)
Repository: https://github.com/eez-open
More info at http://www.envox.hr/eez
12-bit dual DAC with bipolar voltage outputs 8-ch digital low-side power outputs
8-ch digital power outputs
2-ch DAC


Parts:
C75: 100n; C0603
C76: 10u; C1206
C77, C78, C86: 100p; C0805
C79, C80, C81, C82, C83, C84, C85: 10n; C0805
D15, D16, D17, D18, D19, D20, D21, D22: BAT54SFILM; SOT23
IC20: TL431B; SOT103P240X110-3N
Q1, Q2, Q3, Q4, Q5: 2N7002PS,115; SC88
R29: 100R; R0805
R30: 470R; R0805
R31: 1K8; R0805
R32, R33, R34, R35, R36, R37, R38, R39: 2K7; R1206
R40, R41, R42, R43, R44, R45, R46, R47: 27K; R0805
R48, R49, R50, R51, R52, R53, R54, R55: 1K; R0805
X4: 691322310008

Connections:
+3V3_ISO: R29.1; also elsewhere on the board
CLAMP: C75.1, C76.1, D15.2 (C2), D16.2 (C2), D17.2 (C2), D18.2 (C2), D19.2 (C2), D20.2 (C2), D21.2 (C2), D22.2 (C2), IC20.1 (C), R29.2, R30.1; also elsewhere on the board
DIN0: C77.1, C82.1, D15.3 (C1A2), R32.2, R40.2, R48.1; also elsewhere on the board
DIN1: C78.1, C83.1, D16.3 (C1A2), R33.2, R41.2, R49.1; also elsewhere on the board
DIN2: C79.1, D17.3 (C1A2), R34.2, R42.2, R50.1; also elsewhere on the board
DIN3: C84.1, D18.3 (C1A2), R35.2, R43.2, R51.1; also elsewhere on the board
DIN4: C80.1, D19.3 (C1A2), R36.2, R44.2, R52.1; also elsewhere on the board
DIN5: C85.1, D20.3 (C1A2), R37.2, R45.2, R53.1; also elsewhere on the board
DIN6: C81.1, D21.3 (C1A2), R38.2, R46.2, R54.1; also elsewhere on the board
DIN7/MISO: C86.1, D22.3 (C1A2), R39.2, R47.2, R55.1; also elsewhere on the board
GND: C75.2, C76.2, C77.2, C78.2, C79.2, C80.2, C81.2, C84.2, C85.2, C86.2, D15.1 (A1), D16.1 (A1), D17.1 (A1), D18.1 (A1), D19.1 (A1), D20.1 (A1), D21.1 (A1), D22.1 (A1), IC20.3 (A), Q1.1 (S), Q1.4 (S), Q2.1 (S), Q2.4 (S), Q3.1 (S), Q3.4 (S), Q4.1 (S), Q4.4 (S), Q5.1 (S), Q5.4 (S), R31.2, R40.1, R41.1, R42.1, R43.1, R44.1, R45.1, R46.1, R47.1; also elsewhere on the board
IN_CTRL0: Q1.2 (G); also elsewhere on the board
IN_CTRL1: Q1.5 (G); also elsewhere on the board
IN_CTRL2: Q2.2 (G); also elsewhere on the board
IN_CTRL3: Q2.5 (G); also elsewhere on the board
IN_CTRL4: Q3.2 (G); also elsewhere on the board
IN_CTRL5: Q3.5 (G); also elsewhere on the board
IN_CTRL6: Q4.2 (G); also elsewhere on the board
IN_CTRL7: Q4.5 (G); also elsewhere on the board
unnamed: IC20.2 (R), R30.2, R31.1
unnamed: Q1.6 (D), R48.2
unnamed: Q1.3 (D), R49.2
unnamed: Q2.6 (D), R50.2
unnamed: Q2.3 (D), R51.2
unnamed: R33.1, X4.7
unnamed: Q3.6 (D), R52.2
unnamed: Q3.3 (D), R53.2
unnamed: Q4.6 (D), R54.2
unnamed: Q4.3 (D), R55.2
unnamed: C82.2, Q5.6 (D)
unnamed: R32.1, X4.8
unnamed: R34.1, X4.6
unnamed: R35.1, X4.5
unnamed: C83.2, Q5.3 (D)
unnamed: R36.1, X4.4
unnamed: R38.1, X4.2
unnamed: R39.1, X4.1
unnamed: R37.1, X4.3
SLOW_DIN#0: Q5.2 (G); also elsewhere on the board
SLOW_DIN#1: Q5.5 (G); also elsewhere on the board

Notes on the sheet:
Licensed under the TAPR Open Hardware License (www.tapr.org/OHL)
Repository: https://github.com/eez-open
More info at http://www.envox.hr/eez
Digital inputs, two ranges

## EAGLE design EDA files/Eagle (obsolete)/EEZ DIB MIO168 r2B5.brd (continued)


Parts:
C87: 100n; C0603
D23, D24: BAT54SFILM; SOT23
D25, D26: MBR0530T3G; SOD123
IC21: DG212BDY-T1-E3; SO16
IC22: 74HC126PW,118; PW14
JP2, JP3: DS1025-01-1*3P8BV1-B; ZL303-03P
Q6, Q8: BSS84P; SOT95P237X112-3N
Q7: MMBT5401; SOT23-BEC
Q9, Q10: MMBT5551; SOT23-BEC
Q11: 2N7002; SOT103P240X110-3N
R56, R57: 1K; R0805
R58, R59: 100R; R0805
R60, R66: 47R; R0805
R61, R65: 100K; R0805
R62, R64: 10K; R0805
R63: 470R; R0805
X3: 691327310016
X5, X6: DS1014-10RF1B
X7, X8: DS1023-2*14S21; TSW-114-07-F-D
ZD1, ZD2: SMAJ16A; DO214AC

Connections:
!ADC_CS: X7.5; also elsewhere on the board
!ADC_DRDY: X7.7; also elsewhere on the board
!RESET: X7.9; also elsewhere on the board
+3V3_ISO: C87.2, IC22.14 (V+), Q8.2 (S), X7.13; also elsewhere on the board
+5V_ISO: IC21.12 (VL), X7.16; also elsewhere on the board
+15V_ISO: IC21.13 (V+), Q7.E, R60.1, X7.20; also elsewhere on the board
-5V_ISO: X7.15; also elsewhere on the board
-15V_ISO: IC21.4 (V-), Q10.E, R66.1, X7.19; also elsewhere on the board
-VSENSE: IC21.2 (D), IC21.7 (D); also elsewhere on the board
ADC_CLK/SCL1: X7.4; also elsewhere on the board
ADC_MISO: X7.8; also elsewhere on the board
ADC_MOSI: X7.3; also elsewhere on the board
ADC_SCK: X7.6; also elsewhere on the board
ADC_START/SDA1: X7.10; also elsewhere on the board
ADIB1_ID0: X5.7; also elsewhere on the board
ADIB1_ID1: X5.9; also elsewhere on the board
ADIB1_ID2: X5.8; also elsewhere on the board
ADIB1_SW: IC21.1 (IN), IC21.16 (IN); also elsewhere on the board
ADIB2_ID0: X6.7; also elsewhere on the board
ADIB2_ID1: X6.9; also elsewhere on the board
ADIB2_ID2: X6.8; also elsewhere on the board
ADIB2_SW: IC21.8 (IN), IC21.9 (IN); also elsewhere on the board
AFE1N: IC21.3 (S), X5.3, X7.25
AFE1P: R56.1, X5.4, X7.26
AFE2N: IC21.6 (S), X6.3, X7.23
AFE2P: R57.1, X6.4, X7.24
AFE_CLK: X7.14; also elsewhere on the board
AFE_ID0: X8.1; also elsewhere on the board
AFE_ID1: X8.2; also elsewhere on the board
BIAS_EN: R63.1; also elsewhere on the board
CLAMP: D23.2 (C2), D24.2 (C2); also elsewhere on the board
DAC_OUT#1: IC21.15 (D); also elsewhere on the board
DAC_OUT#2: IC21.10 (D); also elsewhere on the board
DOUT_EN: IC22.1 (EN), IC22.4 (EN), IC22.10 (EN), IC22.13 (EN); also elsewhere on the board
GND: C87.1, D23.1 (A1), D24.1 (A1), IC21.5 (GND), IC22.7 (V-), Q9.E, X5.1, X5.2, X5.5, X5.6, X5.10, X6.1, X6.2, X6.5, X6.6, X6.10, X7.1, X7.2, X7.11, X7.12, X7.21, X7.22, X7.27, X7.28, X8.27, X8.28, ZD1.A, ZD2.C; also elsewhere on the board
ISEL10_R#3: X8.21; also elsewhere on the board
ISEL10_R#4: X8.22; also elsewhere on the board
ISEL10_S#3: X8.19; also elsewhere on the board
ISEL10_S#4: X8.20; also elsewhere on the board
ISEL#1: X8.3; also elsewhere on the board
ISEL#2: X8.4; also elsewhere on the board
ISEL_LOW#3: X8.23; also elsewhere on the board
ISEL_LOW#4: X8.24; also elsewhere on the board
ISEL_MID#3: X8.25; also elsewhere on the board
ISEL_MID#4: X8.26; also elsewhere on the board
ISEL_R#3: X8.17; also elsewhere on the board
ISEL_R#4: X8.18; also elsewhere on the board
ISEL_S#3: X8.15; also elsewhere on the board
ISEL_S#4: X8.16; also elsewhere on the board
unnamed: Q9.B, R63.2
unnamed: JP2.1, R58.1
unnamed: JP3.1, R59.1
unnamed: IC21.14 (S), R56.2
unnamed: IC21.11 (S), R57.2
unnamed: JP2.2, X3.6
unnamed: JP3.2, X3.7
unnamed: D23.3 (C1A2), IC22.3 (O), IC22.6 (O), R58.2
unnamed: D24.3 (C1A2), IC22.8 (O), IC22.11 (O), R59.2
unnamed: Q8.1 (G), Q9.C, R62.2
unnamed: Q6.1 (G), Q7.C, R61.2, R62.1
unnamed: D25.A, Q6.3 (D)
unnamed: D25.C, JP2.3, ZD1.C
unnamed: Q6.2 (S), Q7.B, R60.2, R61.1
unnamed: Q10.C, Q11.1 (G), R64.2, R65.1
unnamed: Q10.B, Q11.2 (S), R65.2, R66.2
unnamed: Q8.3 (D), R64.1
unnamed: D26.C, Q11.3 (D)
unnamed: D26.A, JP3.3, ZD2.A
PWM#1/SCK: IC22.2 (I), IC22.5 (I); also elsewhere on the board
PWM#2/MOSI: IC22.9 (I), IC22.12 (I); also elsewhere on the board
USEL1#1: X8.5; also elsewhere on the board
USEL1#2/SDA2: X8.6; also elsewhere on the board
USEL1#3: X8.11; also elsewhere on the board
USEL1#4: X8.12; also elsewhere on the board
USEL10#1: X8.7; also elsewhere on the board
USEL10#2/SCL2: X8.8; also elsewhere on the board
USEL10#3: X8.13; also elsewhere on the board
USEL10#4: X8.14; also elsewhere on the board
USEL100#1: X8.9; also elsewhere on the board
USEL100#2: X8.10; also elsewhere on the board

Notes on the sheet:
Licensed under the TAPR Open Hardware License (www.tapr.org/OHL)
Repository: https://github.com/eez-open
More info at http://www.envox.hr/eez
ADIB switches and AFE connectors PWM outputs / sensor bias
ADIB signal switching
AFE connectors
PWM outputs
Sensor bias outputs



Board: 4 copper layers, 146.0 x 95.0 mm, 257 parts (2 on the bottom side), 251 nets.

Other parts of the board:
EEZ_SIGNATURE: SIGNATURESMALL; SIGNATURE_5MM

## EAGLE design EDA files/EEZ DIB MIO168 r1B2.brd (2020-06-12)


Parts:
C1, C2, C3, C4, C5, C10, C13: 100n; C0603
C6, C12: 4n7/1kV; C1812
C7, C8, C9, C11, C15, C20: 1u; C0805
C14: 2u2; C0805
C16, C18: 4u7; C0805
C17, C19: 10n; C0805
DIB1.1: JP3-CUT-0805-ROTATED; JP3-0805-CUT2
FM1, FM2: FIDUCIAL_2; FIDUCIAL_DUAL
GND: PCB_TEST_TABSHIELD; PCB_SHIELD_TAB
IC1: M24C32-WMN6P; SOIC127P600X173-8N
IC2, IC3: Si8641BB-B-IS1; SOIC-16
IC4: L78L12; SOIC127P600X173-8N
IC5: LP2985-50DBVR; SOT95P270X145-5N
IC6: LP2985-33DBVR; SOT95P270X145-5N
IC7: L79L12; SOIC127P600X173-8N
J1: 4907; PCB_TAB-4907
JP1, JP2: JP2-CUT-0805; R_0805
KK1, KK2: PCB-MB
L1, L2, L3: DLW21SN371SQ2L; MURATA_DLW21S
RN1, RN2: DR1206-33R-4/8; CAY16
RN3: DR1206-10K-4/8; CAY16
TR1: TBA2-1223; TBA2
TR2: MDD02M-15; MDD02
X1: 77317-104-28LF

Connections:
!RESET: IC3.12 (B3); also elsewhere on the board
+3V3: C1.2, C2.1, C4.1, IC1.8 (VCC), IC2.1 (VDD1), IC2.7 (EN1), IC3.1 (VDD1), IC3.7 (EN1), RN3.6 (2), RN3.7 (2), RN3.8 (2), X1.1
+3V3_ISO: C3.2, C5.2, C14.1, IC2.10 (EN2), IC2.16 (VDD2), IC3.10 (EN2), IC3.16 (VDD2), IC6.5 (OUT); also elsewhere on the board
+5V_ISO: C18.2, IC5.5 (OUT), IC6.1 (IN), IC6.3 (ON/!OFF); also elsewhere on the board
+12V: C7.2, L1.4, X1.21, X1.22
+12V_ISO: C10.1, C16.2, IC4.1 (VO), IC5.1 (IN), IC5.3 (ON/!OFF), JP1.2; also elsewhere on the board
+15V_ISO: C11.2, IC4.8 (VI), JP1.1, L2.2; also elsewhere on the board
-12V_ISO: C13.2, IC7.1 (OUT), JP2.2; also elsewhere on the board
-15V_ISO: C15.1, IC7.2 (IN), IC7.3 (IN), IC7.6 (IN), IC7.7 (IN), JP2.1, L3.3; also elsewhere on the board
BOOT0: IC3.13 (B2); also elsewhere on the board
DIB_A0: IC1.1 (A0), RN3.3 (1), X1.17
DIB_A1: IC1.2 (A1), RN3.2 (1), X1.19
DIB_A2: IC1.3 (A2), RN3.1, X1.18
DIB_BOOT: IC3.4 (A2), X1.26
DIB_CSA: IC2.5 (A3), RN2.2 (1)
DIB_CSB: DIB1.1.NO, X1.12
DIB_IRQ: DIB1.1.NC, X1.10
DIB_MISO: IC2.6 (A4), RN2.1
DIB_MOSI: IC2.3 (A1), RN2.4 (1)
DIB_NRESET: IC3.5 (A3), X1.4
DIB_SCL: IC1.6 (SCL), X1.5
DIB_SCLK: IC2.4 (A2), RN2.3 (1)
DIB_SDA: IC1.5 (SDA), X1.8
GND: C3.1, C5.1, C10.2, C11.1, C13.1, C14.2, C15.2, C16.1, C17.1, C18.1, C19.1, GND.1, IC2.9 (GND2_2), IC2.15 (GND2), IC3.9 (GND2_2), IC3.15 (GND2), IC4.2 (GND), IC4.3 (GND), IC4.6 (GND), IC4.7 (GND), IC5.2 (GND), IC6.2 (GND), IC7.5 (GND), L2.3, L3.2; also elsewhere on the board
GNDIO: C1.1, C2.2, C4.2, C7.1, IC1.4 (GND), IC1.7 (WP), IC2.2 (GND1_2), IC2.8 (GND1), IC3.2 (GND1_2), IC3.8 (GND1), L1.1, X1.7, X1.11, X1.16, X1.20, X1.25
IRQ: IC3.11 (B4); also elsewhere on the board
MISO: RN1.6 (2); also elsewhere on the board
MOSI: RN1.5 (2); also elsewhere on the board
unnamed: DIB1.1.COM, IC3.6 (A4)
unnamed: IC2.14 (B1), RN1.4 (1)
unnamed: C9.2, L2.1, TR1.6 (OUT+), TR2.7 (OUT+)
unnamed: C6.2, C9.1, C12.2, C20.2, L2.4, L3.1, TR1.5 (COMM), TR2.6 (COMM)
unnamed: C20.1, L3.4, TR1.4 (OUT-), TR2.5 (OUT-)
unnamed: C6.1, C8.2, L1.3, TR1.1 (IN+), TR2.1 (IN+)
unnamed: C8.1, C12.1, L1.2, TR1.2 (IN-), TR2.2 (IN-)
unnamed: RN2.7 (2), X1.9
unnamed: C17.2, IC5.4 (BYPASS)
unnamed: IC2.11 (B4), RN1.3 (1)
unnamed: RN2.6 (2), X1.13
unnamed: RN2.8 (2), X1.14
unnamed: RN2.5 (2), X1.15
unnamed: C19.2, IC6.4 (BYPASS)
unnamed: IC2.13 (B2), RN1.2 (1)
unnamed: IC2.12 (B3), RN1.1
NSS: RN1.8 (2); also elsewhere on the board
OE_SYNC: IC3.3 (A1), X1.6
PE: J1.1, J1.2; also elsewhere on the board
SCLK: RN1.7 (2); also elsewhere on the board
SYNC: IC3.14 (B1); also elsewhere on the board

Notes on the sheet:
Licensed under the TAPR Open Hardware License (www.tapr.org/OHL)
Repository: https://github.com/eez-open
More info at http://www.envox.hr/eez
DIB, EEPROM, bus isolator, Isolated power supply, LDOs
Plastic parts
I2C Module ID EEPROM
+5V, +3V3 LDO
Bus isolator
Isolated +/-12 V power supply
DIB connector


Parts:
C21: N.C.; C0805
C22, C23: 18p; C0603
C24: 1n; C0805
C25: 4u7; EC1206
C26, C27, C28, C29, C30, C31, C32, C33, C34, C35, C36, C38: 100n; C0603
C37: 1u; C0805
C39, C40: 2u2; C0805
FB1: BLM18AG102SH1D; BEAD0603
IC8: STM32F446ZCT6; LQFP-144
J2: N.C.; 5033981892
R1, R2, R3, R4, R5: N.C.; R0805
R6: 4K7; R0805
R7: 10K; R0805
R8: 47R; R0805
RN4, RN5: DR1206-33R-4/8; CAY16
SH1: SHORTNOHOLE; SHORT_NOHOLE
X2: SSW-106-02-S-S
Y1: 25MHz; HC-49/4H
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

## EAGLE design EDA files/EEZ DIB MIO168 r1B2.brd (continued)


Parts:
C61, C62, C64, C65, C67, C68, C69, C70, C71, C72, C73: 100n; C0603
C63: 150n; C0805
C66: 4u7; C0805
D3, D4, D5, D6: BAT54SFILM; SOT23
FB4: BLM18AG102SH1D; BEAD0603
IC12: OPA376AIDBVR; DBV5
IC13: DAC7563TDGSR; DGS10
IC14: OPA2196IDR; SOIC127P600X173-8N
IC15, IC16, IC17, IC18: BTS3408G; SOIC127P600X173-8N
IC19: 74HC126PW,118; PW14
R16, R18, R21, R22, R24, R28: 9K09 0.1%; R0805
R17, R23, R25, R29: 75K 0.1%; R0805
R19, R26: 180R; R0805
R20, R27: 47R; R0805
R30: 10K; R0805
R31, R32: 100R; R0805
SH4: SHORTNOHOLE; SHORT_NOHOLE
TVS3, TVS4: PESD12VL1BA,115; SOD323-BIDIR
X3: 691327310016

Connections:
1V25_REF: IC12.1 (OUT), IC12.4 (-IN), R16.2, R24.2; also elsewhere on the board
2V5_REF: C63.2, IC13.10 (VREF), R18.1
!DAC_CS_DUAL: IC13.6 (!SYNC); also elsewhere on the board
!OUT_FAULT: IC15.1 (!FAULT), IC16.1 (!FAULT), IC17.1 (!FAULT), IC18.1 (!FAULT), R30.2; also elsewhere on the board
!RESET: IC13.5 (!CLR); also elsewhere on the board
+3V3_ISO: C73.2, FB4.P$2 (2), IC19.14 (V+), R30.1; also elsewhere on the board
+5V_ISO: D5.2 (C2), D6.2 (C2); also elsewhere on the board
+12V_ISO: C61.1, C69.2, C70.2, C71.2, C72.2, D3.2 (C2), D4.2 (C2), IC14.8 (V+), IC15.8 (VSS), IC16.8 (VSS), IC17.8 (VSS), IC18.8 (VSS); also elsewhere on the board
-12V_ISO: C64.1, D3.1 (A1), D4.1 (A1), IC14.4 (V-); also elsewhere on the board
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

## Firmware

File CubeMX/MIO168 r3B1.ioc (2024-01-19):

#MicroXplorer Configuration settings - do not modify
CAD.formats=
CAD.pinconfig=
CAD.provider=
Dma.Request0=SPI3_RX
Dma.Request1=SPI3_TX
Dma.RequestsNb=2
Dma.SPI3_RX.0.Direction=DMA_PERIPH_TO_MEMORY
Dma.SPI3_RX.0.FIFOMode=DMA_FIFOMODE_DISABLE
Dma.SPI3_RX.0.Instance=DMA1_Stream0
Dma.SPI3_RX.0.MemDataAlignment=DMA_MDATAALIGN_BYTE
Dma.SPI3_RX.0.MemInc=DMA_MINC_ENABLE
Dma.SPI3_RX.0.Mode=DMA_NORMAL
Dma.SPI3_RX.0.PeriphDataAlignment=DMA_PDATAALIGN_BYTE
Dma.SPI3_RX.0.PeriphInc=DMA_PINC_DISABLE
Dma.SPI3_RX.0.Priority=DMA_PRIORITY_LOW
Dma.SPI3_RX.0.RequestParameters=Instance,Direction,PeriphInc,MemInc,PeriphDataAlignment,MemDataAlignment,Mode,Priority,FIFOMode
Dma.SPI3_TX.1.Direction=DMA_MEMORY_TO_PERIPH
Dma.SPI3_TX.1.FIFOMode=DMA_FIFOMODE_DISABLE
Dma.SPI3_TX.1.Instance=DMA1_Stream5
Dma.SPI3_TX.1.MemDataAlignment=DMA_MDATAALIGN_BYTE
Dma.SPI3_TX.1.MemInc=DMA_MINC_ENABLE
Dma.SPI3_TX.1.Mode=DMA_NORMAL
Dma.SPI3_TX.1.PeriphDataAlignment=DMA_PDATAALIGN_BYTE
Dma.SPI3_TX.1.PeriphInc=DMA_PINC_DISABLE
Dma.SPI3_TX.1.Priority=DMA_PRIORITY_LOW
Dma.SPI3_TX.1.RequestParameters=Instance,Direction,PeriphInc,MemInc,PeriphDataAlignment,MemDataAlignment,Mode,Priority,FIFOMode
File.Version=6
GPIO.groupedBy=Group By Peripherals
KeepUserPlacement=false
Mcu.CPN=STM32F446ZCT6
Mcu.Family=STM32F4
Mcu.IP0=CRC
Mcu.IP1=DMA
Mcu.IP10=TIM6
Mcu.IP11=TIM7
Mcu.IP12=TIM9
Mcu.IP2=FMC
Mcu.IP3=NVIC
Mcu.IP4=RCC
Mcu.IP5=SPI2
Mcu.IP6=SPI3
Mcu.IP7=SYS
Mcu.IP8=TIM2
Mcu.IP9=TIM3
Mcu.IPNb=13
Mcu.Name=STM32F446Z(C-E)Tx
Mcu.Package=LQFP144
Mcu.Pin0=PE2
Mcu.Pin1=PE3
Mcu.Pin10=PF2
Mcu.Pin100=PG11
Mcu.Pin101=PG12
Mcu.Pin102=PG13
Mcu.Pin103=PG14
Mcu.Pin104=PG15
Mcu.Pin105=PB3
Mcu.Pin106=PB4
Mcu.Pin107=PB5
Mcu.Pin108=PB6
Mcu.Pin109=PB7
Mcu.Pin11=PF3
Mcu.Pin110=PB8
Mcu.Pin111=PB9
Mcu.Pin112=PE0
Mcu.Pin113=PE1
Mcu.Pin114=VP_CRC_VS_CRC
Mcu.Pin115=VP_SYS_VS_Systick
Mcu.Pin116=VP_TIM6_VS_ClockSourceINT
Mcu.Pin117=VP_TIM7_VS_ClockSourceINT
Mcu.Pin12=PF4
Mcu.Pin13=PF5
Mcu.Pin14=PF6
Mcu.Pin15=PF7
Mcu.Pin16=PF8
Mcu.Pin17=PF9
Mcu.Pin18=PF10
Mcu.Pin19=PH0-OSC_IN
Mcu.Pin2=PE4
Mcu.Pin20=PH1-OSC_OUT
Mcu.Pin21=PC0
Mcu.Pin22=PC1
Mcu.Pin23=PC2
Mcu.Pin24=PC3
Mcu.Pin25=PA0-WKUP
Mcu.Pin26=PA1
Mcu.Pin27=PA2
Mcu.Pin28=PA3
Mcu.Pin29=PA4
Mcu.Pin3=PE5
Mcu.Pin30=PA5
Mcu.Pin31=PA6
Mcu.Pin32=PA7
Mcu.Pin33=PC4
Mcu.Pin34=PC5
Mcu.Pin35=PB0
Mcu.Pin36=PB1
Mcu.Pin37=PB2
Mcu.Pin38=PF11
Mcu.Pin39=PF12
Mcu.Pin4=PE6
Mcu.Pin40=PF13
Mcu.Pin41=PF14
Mcu.Pin42=PF15
Mcu.Pin43=PG0
Mcu.Pin44=PG1
Mcu.Pin45=PE7
Mcu.Pin46=PE8
Mcu.Pin47=PE9
Mcu.Pin48=PE10
Mcu.Pin49=PE11
Mcu.Pin5=PC13
Mcu.Pin50=PE12
Mcu.Pin51=PE13
Mcu.Pin52=PE14
Mcu.Pin53=PE15
Mcu.Pin54=PB10
Mcu.Pin55=PB11
Mcu.Pin56=PB12
Mcu.Pin57=PB13
Mcu.Pin58=PB14
Mcu.Pin59=PB15
Mcu.Pin6=PC14-OSC32_IN
Mcu.Pin60=PD8
Mcu.Pin61=PD9
Mcu.Pin62=PD10
Mcu.Pin63=PD11
Mcu.Pin64=PD12
Mcu.Pin65=PD13
Mcu.Pin66=PD14
Mcu.Pin67=PD15
Mcu.Pin68=PG2
Mcu.Pin69=PG3
Mcu.Pin7=PC15-OSC32_OUT
Mcu.Pin70=PG4
Mcu.Pin71=PG5
Mcu.Pin72=PG6
Mcu.Pin73=PG7
Mcu.Pin74=PG8
Mcu.Pin75=PC6
Mcu.Pin76=PC7
Mcu.Pin77=PC8
Mcu.Pin78=PC9
Mcu.Pin79=PA8
Mcu.Pin8=PF0
Mcu.Pin80=PA9
Mcu.Pin81=PA10
Mcu.Pin82=PA11
Mcu.Pin83=PA12
Mcu.Pin84=PA13
Mcu.Pin85=PA14
Mcu.Pin86=PA15
Mcu.Pin87=PC10
Mcu.Pin88=PC11
Mcu.Pin89=PC12
Mcu.Pin9=PF1
Mcu.Pin90=PD0
Mcu.Pin91=PD1
Mcu.Pin92=PD2
Mcu.Pin93=PD3
Mcu.Pin94=PD4
Mcu.Pin95=PD5
Mcu.Pin96=PD6
Mcu.Pin97=PD7
Mcu.Pin98=PG9
Mcu.Pin99=PG10
Mcu.PinsNb=118
Mcu.ThirdPartyNb=0
Mcu.UserConstants=
Mcu.UserName=STM32F446ZCTx
MxCube.Version=6.10.0
MxDb.Version=DB.6.0.100
NVIC.BusFault_IRQn=true\:0\:0\:false\:false\:true\:false\:false\:false
NVIC.DMA1_Stream0_IRQn=true\:0\:0\:true\:false\:true\:false\:true\:true
NVIC.DMA1_Stream5_IRQn=true\:0\:0\:true\:false\:true\:false\:true\:true
NVIC.DebugMonitor_IRQn=true\:0\:0\:false\:false\:true\:false\:false\:false
NVIC.ForceEnableDMAVector=true
NVIC.HardFault_IRQn=true\:0\:0\:false\:false\:true\:false\:false\:false
NVIC.MemoryManagement_IRQn=true\:0\:0\:false\:false\:true\:false\:false\:false
NVIC.NonMaskableInt_IRQn=true\:0\:0\:false\:false\:true\:false\:false\:false
NVIC.PendSV_IRQn=true\:0\:0\:false\:false\:true\:false\:false\:false
NVIC.PriorityGroup=NVIC_PRIORITYGROUP_4
NVIC.SVCall_IRQn=true\:0\:0\:false\:false\:true\:false\:false\:false
NVIC.SysTick_IRQn=true\:0\:0\:false\:false\:true\:false\:true\:false
NVIC.TIM6_DAC_IRQn=true\:0\:0\:false\:false\:true\:true\:true\:true
NVIC.TIM7_IRQn=true\:0\:0\:true\:false\:true\:true\:true\:true
NVIC.UsageFault_IRQn=true\:0\:0\:false\:false\:true\:false\:false\:false
PA0-WKUP.GPIOParameters=GPIO_Speed,GPIO_Label
PA0-WKUP.GPIO_Label=DOUT0
PA0-WKUP.GPIO_Speed=GPIO_SPEED_FREQ_LOW
PA0-WKUP.Locked=true
PA0-WKUP.Signal=GPIO_Output
PA1.GPIOParameters=GPIO_Label
PA1.GPIO_Label=DOUT1
PA1.Locked=true
PA1.Signal=GPIO_Output
PA10.GPIOParameters=GPIO_Label
PA10.GPIO_Label=ADIB2_SW
PA10.Locked=true
PA10.Signal=GPIO_Output
PA11.GPIOParameters=GPIO_Label
PA11.GPIO_Label=ISEL_LOW\#4
PA11.Locked=true
PA11.Signal=GPIO_Output
PA12.GPIOParameters=GPIO_Label
PA12.GPIO_Label=ISEL_MID\#4
PA12.Locked=true
PA12.Signal=GPIO_Output
PA13.Mode=Serial_Wire
PA13.Signal=SYS_JTMS-SWDIO
PA14.Mode=Serial_Wire
PA14.Signal=SYS_JTCK-SWCLK
PA15.GPIOParameters=GPIO_Speed,PinState,GPIO_Label
PA15.GPIO_Label=USEL100\#2
PA15.GPIO_Speed=GPIO_SPEED_FREQ_LOW
PA15.Locked=true
PA15.PinState=GPIO_PIN_SET
PA15.Signal=GPIO_Output
PA2.GPIOParameters=GPIO_Label
PA2.GPIO_Label=DOUT2
PA2.Locked=true
PA2.Signal=GPIO_Output
PA3.GPIOParameters=GPIO_Label
PA3.GPIO_Label=DOUT3
PA3.Locked=true
PA3.Signal=GPIO_Output
PA4.GPIOParameters=GPIO_Label
PA4.GPIO_Label=SLOW_DIN
PA4.Locked=true
PA4.Signal=GPIO_Output
PA5.GPIOParameters=GPIO_Label
PA5.GPIO_Label=PWM1
PA5.Locked=true
PA5.Signal=S_TIM2_CH1_ETR
PA6.GPIOParameters=GPIO_Label
PA6.GPIO_Label=DIN7
PA6.Locked=true
PA6.Signal=GPIO_Input
PA7.GPIOParameters=GPIO_Label
PA7.GPIO_Label=PWM2
PA7.Locked=true
PA7.Signal=S_TIM3_CH2
PA8.GPIOParameters=GPIO_Label
PA8.GPIO_Label=ISEL10_S\#4
PA8.Locked=true
PA8.Signal=GPIO_Output
PA9.GPIOParameters=GPIO_Label
PA9.GPIO_Label=ISEL10_R\#4
PA9.Locked=true
PA9.Signal=GPIO_Output
PB0.GPIOParameters=GPIO_Label
PB0.GPIO_Label=DOUT6
PB0.Locked=true
PB0.Signal=GPIO_Output
PB1.GPIOParameters=GPIO_Label
PB1.GPIO_Label=DOUT7
PB1.Locked=true
PB1.Signal=GPIO_Output
PB10.GPIOParameters=GPIO_Label
PB10.GPIO_Label=USEL20\#2
PB10.Locked=true
PB10.Signal=GPIO_Output
PB11.GPIOParameters=GPIO_Label
PB11.GPIO_Label=USEL1\#2
PB11.Locked=true
PB11.Signal=GPIO_Output
PB12.GPIOParameters=GPIO_Label
PB12.GPIO_Label=DIB_NSS
PB12.Mode=NSS_Signal_Hard_Input
PB12.Signal=SPI2_NSS
PB13.GPIOParameters=GPIO_Label
PB13.GPIO_Label=ADIB2_ID0
PB13.Locked=true
PB13.Signal=GPIO_Input
PB14.GPIOParameters=GPIO_Label
PB14.GPIO_Label=DIB_MISO
PB14.Locked=true
PB14.Mode=Full_Duplex_Slave
PB14.Signal=SPI2_MISO
PB15.GPIOParameters=GPIO_Label
PB15.GPIO_Label=DIB_MOSI
PB15.Locked=true
PB15.Mode=Full_Duplex_Slave
PB15.Signal=SPI2_MOSI
PB2.GPIOParameters=GPIO_Label
PB2.GPIO_Label=ADC_DRDY
PB2.Locked=true
PB2.Signal=GPIO_Input
PB3.GPIOParameters=GPIO_Label
PB3.GPIO_Label=MIO_SCK
PB3.Mode=Full_Duplex_Master
PB3.Signal=SPI3_SCK
PB4.GPIOParameters=GPIO_Label
PB4.GPIO_Label=MIO_MISO
PB4.Mode=Full_Duplex_Master
PB4.Signal=SPI3_MISO
PB5.GPIOParameters=GPIO_Label
PB5.GPIO_Label=MIO_MOSI
PB5.Locked=true
PB5.Mode=Full_Duplex_Master
PB5.Signal=SPI3_MOSI
PB6.GPIOParameters=GPIO_Label
PB6.GPIO_Label=ADC_START/SCL1
PB6.Locked=true
PB6.Signal=GPIO_Output
PB7.GPIOParameters=GPIO_Label
PB7.GPIO_Label=ADC_CLK/SDA1
PB7.Locked=true
PB7.Signal=GPIO_Output
PB8.GPIOParameters=GPIO_Label
PB8.GPIO_Label=LEVEL_DIN0_3
PB8.Locked=true
PB8.Signal=GPIO_Output
PB9.GPIOParameters=GPIO_Label
PB9.GPIO_Label=LEVEL_DIN3_7
PB9.Locked=true
PB9.Signal=GPIO_Output
PC0.Signal=FMC_SDNWE
PC1.GPIOParameters=GPIO_Label
PC1.GPIO_Label=ADIB2_ID1
PC1.Locked=true
PC1.Signal=GPIO_Input
PC10.GPIOParameters=GPIO_Label
PC10.GPIO_Label=USEL20\#3
PC10.Locked=true
PC10.Signal=GPIO_Output
PC11.GPIOParameters=GPIO_Label
PC11.GPIO_Label=USEL1\#3
PC11.Locked=true
PC11.Signal=GPIO_Output
PC12.GPIOParameters=GPIO_Label
PC12.GPIO_Label=DAC_ALARM
PC12.Locked=true
PC12.Signal=GPIO_Input
PC13.GPIOParameters=GPIO_Label
PC13.GPIO_Label=USEL1\#4
PC13.Locked=true
PC13.Signal=GPIO_Output
PC14-OSC32_IN.GPIOParameters=GPIO_Label
PC14-OSC32_IN.GPIO_Label=USEL20\#4
PC14-OSC32_IN.Locked=true
PC14-OSC32_IN.Signal=GPIO_Output
PC15-OSC32_OUT.GPIOParameters=GPIO_Label
PC15-OSC32_OUT.GPIO_Label=ISEL\#2
PC15-OSC32_OUT.Locked=true
PC15-OSC32_OUT.Signal=GPIO_Output
PC2.Mode=SdramChipSelect1_1
PC2.Signal=FMC_SDNE0
PC3.Mode=SdramChipSelect1_1
PC3.Signal=FMC_SDCKE0
PC4.GPIOParameters=GPIO_Label
PC4.GPIO_Label=DOUT4
PC4.Locked=true
PC4.Signal=GPIO_Output
PC5.GPIOParameters=GPIO_Label
PC5.GPIO_Label=DOUT5
PC5.Locked=true
PC5.Signal=GPIO_Output
PC6.GPIOParameters=GPIO_Label
PC6.GPIO_Label=ISEL_R\#4
PC6.Locked=true
PC6.Signal=GPIO_Output
PC7.GPIOParameters=GPIO_Label
PC7.GPIO_Label=DIB_SCK
PC7.Locked=true
PC7.Mode=Full_Duplex_Slave
PC7.Signal=SPI2_SCK
PC8.GPIOParameters=GPIO_Label
PC8.GPIO_Label=ISEL_S\#4
PC8.Locked=true
PC8.Signal=GPIO_Output
PC9.GPIOParameters=GPIO_Label
PC9.GPIO_Label=AFE_CLK
PC9.Mode=Clock-out-2
PC9.Signal=RCC_MCO_2
PD0.Signal=FMC_D2_DA2
PD1.Signal=FMC_D3_DA3
PD10.Signal=FMC_D15_DA15
PD11.GPIOParameters=GPIO_PuPd,GPIO_Label
PD11.GPIO_Label=ADIB1_ID2
PD11.GPIO_PuPd=GPIO_PULLUP
PD11.Locked=true
PD11.Signal=GPIO_Input
PD12.GPIOParameters=GPIO_PuPd,GPIO_Label
PD12.GPIO_Label=ADIB1_ID1
PD12.GPIO_PuPd=GPIO_PULLUP
PD12.Locked=true
PD12.Signal=GPIO_Input
PD13.GPIOParameters=GPIO_PuPd,GPIO_Label
PD13.GPIO_Label=ADIB1_ID0
PD13.GPIO_PuPd=GPIO_PULLUP
PD13.Locked=true
PD13.Signal=GPIO_Input
PD14.Signal=FMC_D0_DA0
PD15.Signal=FMC_D1_DA1
PD2.GPIOParameters=GPIO_Label
PD2.GPIO_Label=BIAS_EN
PD2.Locked=true
PD2.Signal=GPIO_Output
PD3.GPIOParameters=GPIO_Label
PD3.GPIO_Label=ADIB1_SW
PD3.Locked=true
PD3.Signal=GPIO_Output
PD4.GPIOParameters=GPIO_Label
PD4.GPIO_Label=ISEL_MID\#3
PD4.Locked=true
PD4.Signal=GPIO_Output
PD5.GPIOParameters=GPIO_Label
PD5.GPIO_Label=ISEL_LOW\#3
PD5.Locked=true
PD5.Signal=GPIO_Output
PD6.GPIOParameters=GPIO_Label
PD6.GPIO_Label=ISEL10_R\#3
PD6.Locked=true
PD6.Signal=GPIO_Output
PD7.GPIOParameters=GPIO_Label
PD7.GPIO_Label=ISEL10_S\#3
PD7.Locked=true
PD7.Signal=GPIO_Output
PD8.Signal=FMC_D13_DA13
PD9.Signal=FMC_D14_DA14
PE0.Signal=FMC_NBL0
PE1.Signal=FMC_NBL1
PE10.Signal=FMC_D7_DA7
PE11.Signal=FMC_D8_DA8
PE12.Signal=FMC_D9_DA9
PE13.Signal=FMC_D10_DA10
PE14.Signal=FMC_D11_DA11
PE15.Signal=FMC_D12_DA12
PE2.GPIOParameters=GPIO_Label
PE2.GPIO_Label=DIN4
PE2.Locked=true
PE2.Signal=GPIO_Input
PE3.GPIOParameters=GPIO_Label
PE3.GPIO_Label=DIN3
PE3.Locked=true
PE3.Signal=GPIO_Input
PE4.GPIOParameters=GPIO_Label
PE4.GPIO_Label=DIN2
PE4.Locked=true
PE4.Signal=GPIO_Input
PE5.GPIOParameters=GPIO_Label
PE5.GPIO_Label=DIN1
PE5.Locked=true
PE5.Signal=S_TIM9_CH1
PE6.GPIOParameters=GPIO_Label
PE6.GPIO_Label=DIN0
PE6.Locked=true
PE6.Signal=S_TIM9_CH2
PE7.Signal=FMC_D4_DA4
PE8.Signal=FMC_D5_DA5
PE9.Signal=FMC_D6_DA6
PF0.Signal=FMC_A0
PF1.Signal=FMC_A1
PF10.GPIOParameters=GPIO_Label
PF10.GPIO_Label=DIB_IRQ
PF10.Locked=true
PF10.Signal=GPIO_Output
PF11.Signal=FMC_SDNRAS
PF12.Signal=FMC_A6
PF13.Signal=FMC_A7
PF14.Signal=FMC_A8
PF15.Signal=FMC_A9
PF2.Signal=FMC_A2
PF3.Signal=FMC_A3
PF4.Signal=FMC_A4
PF5.Signal=FMC_A5
PF6.GPIOParameters=GPIO_Label
PF6.GPIO_Label=DIN5
PF6.Locked=true
PF6.Signal=GPIO_Input
PF7.GPIOParameters=GPIO_Label
PF7.GPIO_Label=DIN6
PF7.Locked=true
PF7.Signal=GPIO_Input
PF8.GPIOParameters=GPIO_Label
PF8.GPIO_Label=DIB_SYNC
PF8.Locked=true
PF8.Signal=GPIO_Input
PF9.GPIOParameters=GPIO_Label
PF9.GPIO_Label=ADIB2_ID2
PF9.Locked=true
PF9.Signal=GPIO_Input
PG0.Signal=FMC_A10
PG1.Locked=true
PG1.Signal=FMC_A11
PG10.GPIOParameters=GPIO_Label
PG10.GPIO_Label=ISEL_S\#3
PG10.Locked=true
PG10.Signal=GPIO_Output
PG11.GPIOParameters=GPIO_Label
PG11.GPIO_Label=USEL100\#1
PG11.Locked=true
PG11.Signal=GPIO_Output
PG12.GPIOParameters=GPIO_Label
PG12.GPIO_Label=USEL20\#1
PG12.Locked=true
PG12.Signal=GPIO_Output
PG13.GPIOParameters=GPIO_Label
PG13.GPIO_Label=USEL1\#1
PG13.Locked=true
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

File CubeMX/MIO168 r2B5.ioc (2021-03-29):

#MicroXplorer Configuration settings - do not modify
Dma.SDIO_RX.4.MemBurst=DMA_MBURST_INC4
PB13.GPIOParameters=GPIO_Label
PD12.GPIO_Label=ADIB1_ID1
PC7.GPIOParameters=GPIO_Label
FATFS._USE_LFN=2
PE11.GPIOParameters=GPIO_Label
FATFS0.BSP.api=Unknown
NVIC.TIM6_DAC_IRQn=true\:0\:0\:false\:false\:true\:true\:true
PF14.PinState=GPIO_PIN_SET
PG8.Signal=GPIO_Output
Dma.SPI4_TX.1.PeriphDataAlignment=DMA_PDATAALIGN_BYTE
PG8.Locked=true
PG0.Locked=true
RCC.PLLQCLKFreq_Value=45000000
PG0.Signal=GPXTI0
PC7.Locked=true
PD8.Locked=true
PD0.Locked=true
PG14.GPIOParameters=GPIO_Label
PA2.GPIOParameters=GPIO_Label
PG2.GPIOParameters=GPIO_PuPd,GPIO_Label
Dma.SPI4_RX.0.RequestParameters=Instance,Direction,PeriphInc,MemInc,PeriphDataAlignment,MemDataAlignment,Mode,Priority,FIFOMode
NVIC.SVCall_IRQn=true\:0\:0\:false\:false\:true\:false\:false
PG15.GPIO_Label=ADC_DRDY
SH.S_TIM3_CH2.ConfNb=1
RCC.APB2TimFreq_Value=180000000
SDIO.IPParameters=ClockBypass,HardwareFlowControl,ClockDiv
PB6.Signal=GPIO_Output
PC7.Signal=GPIO_Output
PB12.PinState=GPIO_PIN_SET
PD0.Signal=GPIO_Output
Dma.SPI3_RX.6.Direction=DMA_PERIPH_TO_MEMORY
PD8.Signal=GPXTI8
PE1.Signal=GPIO_Input
Dma.SPI4_RX.0.Priority=DMA_PRIORITY_LOW
FATFS0.BSP.ip=GPIO
PE14.Locked=true
NVIC.EXTI15_10_IRQn=true\:0\:0\:false\:false\:true\:true\:true
ProjectManager.ProjectBuild=false
Dma.SPI2_RX.2.MemDataAlignment=DMA_MDATAALIGN_HALFWORD
NVIC.UsageFault_IRQn=true\:0\:0\:false\:false\:true\:false\:false
Dma.SPI3_RX.6.Mode=DMA_NORMAL
PB3.Mode=Full_Duplex_Master
PF1.GPIO_Label=USEL10\#2
Dma.SPI2_RX.2.PeriphInc=DMA_PINC_DISABLE
PD1.GPIO_Label=USEL1\#3
PB12.GPIO_Label=DAC_CS_DUAL
ProjectManager.FirmwarePackage=STM32Cube FW_F4 V1.26.0
PF12.GPIO_Label=DAC_CLR\#1
ProjectManager.BackupPrevious=false
PC4.GPIO_Label=DOUT4
PE9.Signal=GPIO_Input
PG12.GPIOParameters=GPIO_Label
PE9.Locked=true
PB14.Mode=Full_Duplex_Master
PB1.GPIO_Label=DOUT7
PG4.GPIO_Label=IN_CTRL6
PE4.GPIO_Label=DIN2
PC9.Mode=SD_4_bits_Wide_bus
PF13.Locked=true
Dma.SPI2_RX.2.PeriphDataAlignment=DMA_PDATAALIGN_HALFWORD
PD14.GPIO_PuPd=GPIO_PULLUP
PF2.Locked=true
RCC.PLLRCLKFreq_Value=180000000
PE13.Mode=Full_Duplex_Slave
PE1.Locked=true
PB6.Locked=true
PG0.GPIO_PuPd=GPIO_PULLUP
RCC.PLLI2SoutputFreq_Value=96000000
ProjectManager.HalAssertFull=false
Dma.SDIO_TX.5.PeriphDataAlignment=DMA_PDATAALIGN_WORD
Mcu.Package=LQFP144
PB9.Signal=GPIO_Output
PB1.Signal=GPIO_Output
PA5.Locked=true
SPI2.Mode=SPI_MODE_MASTER
Dma.SPI3_RX.6.MemInc=DMA_MINC_ENABLE
RCC.I2S2Freq_Value=96000000
SPI3.Mode=SPI_MODE_MASTER
SH.GPXTI8.0=GPIO_EXTI8
PD12.Signal=GPIO_Input
VP_SYS_VS_Systick.Signal=SYS_VS_Systick
PA10.Signal=GPIO_Output
PE12.GPIO_Label=DIB_SCLK
PC11.Mode=SD_4_bits_Wide_bus
RCC.APB2CLKDivider=RCC_HCLK_DIV2
Dma.SDIO_RX.4.PeriphDataAlignment=DMA_PDATAALIGN_WORD
RCC.APB1TimFreq_Value=90000000
PB13.Mode=Full_Duplex_Master
PE6.Locked=true
PD5.Locked=true
PA4.GPIO_Label=DOUT_EN
PD15.Signal=GPIO_Input
RCC.PLLSAIQCLKFreq_Value=96000000
PG12.Signal=GPIO_Output
PE12.Mode=Full_Duplex_Slave
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

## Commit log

2020-03-09 IC36 name, value added
    [EEZ DIB MIO168 r1B1 raw.csv, EEZ DIB MIO168 r1B1.GBL, EEZ DIB MIO168 r1B1.GBO, EEZ DIB MIO168 r1B1.GBS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]
2020-03-10 BOM added
    [EEZ DIB MIO168 r1B1 raw.csv, EEZ DIB MIO168 r1B1.GBL, EEZ DIB MIO168 r1B1.GTL, EEZ DIB MIO168 r1B1.GTO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]
2020-03-10 PWM outputs clamp fix
    [EEZ DIB MIO168 r1B1.GBL, EEZ DIB MIO168 r1B1.GTL, EEZ DIB MIO168 r1B1.GTO, EEZ DIB MIO168 r1B1.GTS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]
2020-03-10 Vref selection for NTC bias (JP3)
    [EEZ DIB MIO168 r1B1.GBL, EEZ DIB MIO168 r1B1.GTL, EEZ DIB MIO168 r1B1.GTO, EEZ DIB MIO168 r1B1.GTS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]
2020-03-14 Changes suggested by @jbb
    [EEZ DIB MIO168 r1B1.GBL, EEZ DIB MIO168 r1B1.GBS, EEZ DIB MIO168 r1B1.GTL, EEZ DIB MIO168 r1B1.GTO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]
2020-03-15 2N7002PS package fixed
    [EEZ DIB MIO168 r1B1.GBL, EEZ DIB MIO168 r1B1.GTL, EEZ DIB MIO168 r1B1.GTO, EEZ DIB MIO168 r1B1.GTS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]
2020-03-15 PCB preview update
2020-03-19 front panel connectors position adjusted
    [EEZ DIB MIO168 r1B1.GBL, EEZ DIB MIO168 r1B1.GBS, EEZ DIB MIO168 r1B1.GTL, EEZ DIB MIO168 r1B1.GTO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]
2020-04-06 #1 fixed
    [EEZ DIB MIO168 r1B1.GTO, EEZ DIB MIO168 r1B1.ods, EEZ DIB MIO168 r1B2.GBL, EEZ DIB MIO168 r1B2.GBO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]
2020-05-05 Slave SPI moved to SPI4
    [EEZ DIB MIO168 r1B2.GBL, EEZ DIB MIO168 r1B2.GBO, EEZ DIB MIO168 r1B2.GBS, EEZ DIB MIO168 r1B2.GTL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]
2020-05-18 prototype picture
2020-06-12 IRQ selection jumper
    [EEZ DIB MIO168 r1B2.GBL, EEZ DIB MIO168 r1B2.GTL, EEZ DIB MIO168 r1B2.GTO, EEZ DIB MIO168 r1B2.GTS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]
2020-08-27 Connectors for piggyback, GND and PWM outputs jumpers
    [EEZ DIB MIO168 r1B2.GTL, EEZ DIB MIO168 r1B2.GTO, EEZ DIB MIO168 r1B2.GTS, EEZ DIB MIO168 r1B5.GBL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]
2020-09-09 MCU Vdd update
    [EEZ DIB MIO168 r1B5.GBL, EEZ DIB MIO168 r1B5.GTL, EEZ DIB MIO168 r1B5.brd, EEZ DIB MIO168 r1B5.sch]
2020-10-11 #4, BOM update
    [EEZ DIB MIO168 r1B2.ods, EEZ DIB MIO168 r1B5.GBL, EEZ DIB MIO168 r1B5.GBO, EEZ DIB MIO168 r1B5.GBS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]
2020-10-17 ZD1, ZD2 added
    [EEZ DIB MIO168 r1B5.GBL, EEZ DIB MIO168 r1B5.GBS, EEZ DIB MIO168 r1B5.GTL, EEZ DIB MIO168 r1B5.GTO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]
2020-10-31 PWM outputs pin rearrangement
    [EEZ DIB MIO168 r1B5.GBL, EEZ DIB MIO168 r1B5.GBO, EEZ DIB MIO168 r1B5.GBS, EEZ DIB MIO168 r1B5.GTL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]
2020-10-31 swap DOUT0 and DOUT1
    [EEZ DIB MIO168 r1B5.GBL, EEZ DIB MIO168 r1B5.GTL, EEZ DIB MIO168 r1B5.brd, EEZ DIB MIO168 r1B5.sch]
2021-01-22 r2B4 version
    [EEZ DIB MIO168 r1B5.GBL, EEZ DIB MIO168 r1B5.GBO, EEZ DIB MIO168 r1B5.GBS, EEZ DIB MIO168 r1B5.GKO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]
2021-01-31 PCB ID added
    [EEZ DIB MIO168 r2B4.GTL, EEZ DIB MIO168 r2B4.brd, EEZ DIB MIO168 r2B4.sch]
2021-02-07 BOM update
    [EEZ DIB MIO168 r1B5.ods, EEZ DIB MIO168 r2B4.ods]
2021-03-29 r2B5, ADIB switcing
    [EEZ DIB MIO168 r2B4.GTL, EEZ DIB MIO168 r2B4.GTO, EEZ DIB MIO168 r2B4.GTS, EEZ DIB MIO168 r2B4.ods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]
2021-03-29 BOM, .ioc update
    [EEZ DIB MIO168 r2B5.ods]
2021-06-04 DIN3 PCB correction
    [EEZ DIB MIO168 r2B5.GBL, EEZ DIB MIO168 r2B5.GBO, EEZ DIB MIO168 r2B5.GTO, EEZ DIB MIO168 r2B5.brd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]
2024-01-19 #6, #7, r1B3 (KiCad)
    [ADIB_PWM.kicad_sch, DIB_interface.kicad_sch, Digital_inputs.kicad_sch, EEZ DIB MIO168 r2B5 BOM.ods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]
2024-01-20 PCB preview correction

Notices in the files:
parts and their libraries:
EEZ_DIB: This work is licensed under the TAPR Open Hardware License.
